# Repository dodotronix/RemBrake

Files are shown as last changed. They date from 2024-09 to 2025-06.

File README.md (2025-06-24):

# RemBrake - remote brake system for handbikes 

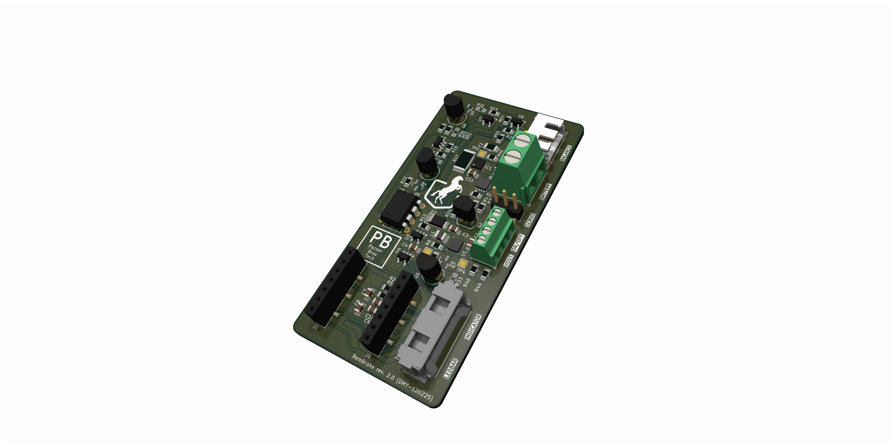
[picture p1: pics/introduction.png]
PCB picture


## Introduction
- TODO explain what the RemBrake, why we decided to create this project

### Assembling RemBrake
- TODO explain how to use the kicad data
- TODO how to solder the modules on the RemBrake PCB
- TODO how to connect the wires

### Prepare the module 
1) load the circuitpython to the QT Py RP2040
2) press and hold BOOT button and then press RST button
3) you should see now RPI partition mounted to your PC 
4) download CircuitPython bootloader (.uf2 file) from [circuitpython.org](https://circuitpython.org/board/adafruit_qtpy_rp2040/) 
5) drag and drop the file onto the partition
6) it takes few moments and you should see your partition name turn to CIRCUITPYTHON

### Upload RemBrake files + necessary modules
1) go to the folder fw folder
2) run $ make prepare
3) move the folder target to your CIRCPITPYTHON partition

## Features
- TODO how the PCB behaves (charging, running, error)
- TODO what the different colors mean

## Possible further development
- Bidirectional remote contoller that the assistant can see the battery status
- Accelerometer feedback, to adjust braking power according to the situation
- Using hydraulic piston actuator to move with the brake directly, which could shrink significantly the size of the package
- designing custom usb-c charger to avoid the hustle with unprecise power management of the chinese module

## Development
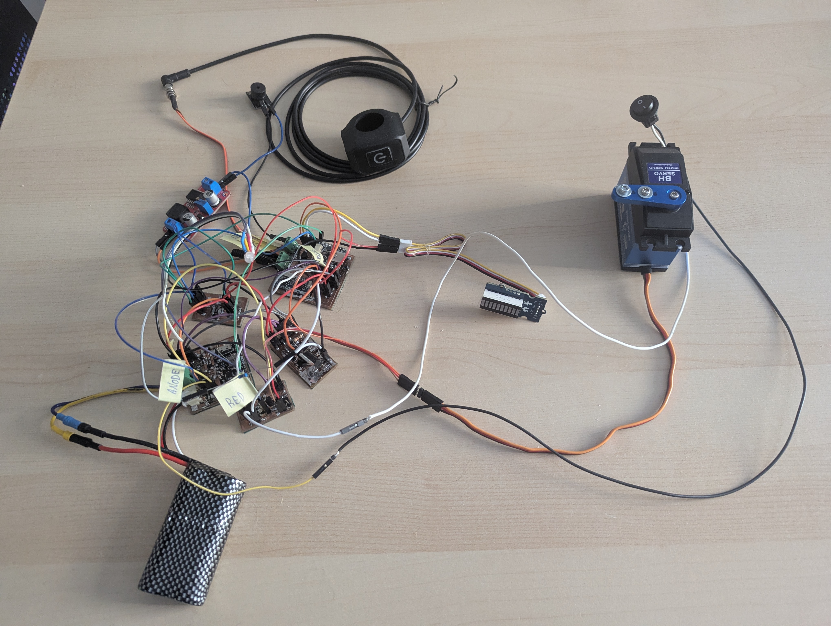
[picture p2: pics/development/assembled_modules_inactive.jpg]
PCB inactive breakout modules

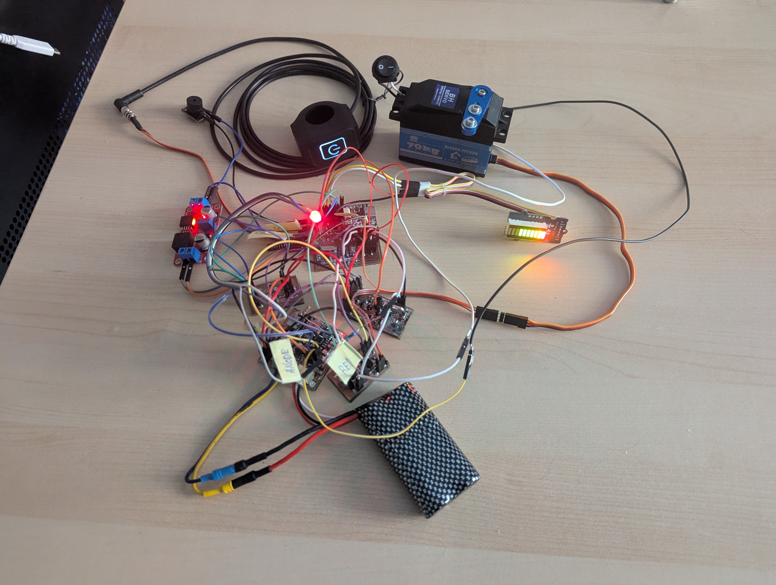
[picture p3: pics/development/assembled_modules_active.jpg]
PCB active breakout modules


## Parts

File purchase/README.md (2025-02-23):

# Shopping List 

The RemBrake requires a few types of electronic components. These can be
purchased on [farnell.com](farnell.com). A pre-prepared list is already available in the user
space—just click on "Purchase." We designed this board using only components
available there. While we cannot guarantee their availability in the future, as
of 2025, they are all in stock.

We decided to use Farnell due to delivery issues with Mouser. The remaining
components are mainly available on AliExpress. The shopping list is below.

| Product | Description | ID | Place to buy | ~price |
|:----:|:----:|:----:|:----:|:----:|
| MCU module | PyQt RP2040 circuitpython supported platform | ADA048 | [link](https://rpishop.cz/adafruit/4248-adafruit-qt-py-rp2040.html) | 349 CZK | 
| USB-C battery charger | Type-C USB 2S BMS 15W 8.4V 1.5A Lithium Battery Charging Boost Module| 2S 8.4V Balanced | [link](https://www.aliexpress.com/item/1005004682732678.html?spm=a2g0o.detail.similar_items.1.16cc8NKk8NKkxb&utparam-url=scene%3Aimage_search%7Cquery_from%3Adetail_bigimg&algo_pvid=c14208da-fe99-42b6-8ce6-5573abc3a80f&algo_exp_id=c14208da-fe99-42b6-8ce6-5573abc3a80f&pdp_ext_f=%7B%22order%22%3A%22200%22%7D&pdp_npi=4%40dis%21CZK%2115.17%2115.17%21%21%210.62%210.62%21%40210390c917403219859821546e6282%2112000030086170587%21sea%21CZ%212328287499%21X) | 15.17 CZK |
| RF transmitter | 1 Channel Wireless RF Remote Control with EV1527 Code, 433 MHz | 1 | [link](https://www.aliexpress.com/item/1005004808801287.html?spm=a2g0o.order_detail.order_detail_item.3.8201f19ccRamzA) | 66.78 CZK |
| RF receiver | 433mhz RF Receiver Learning Code Decoder Module 433 mhz Wireless | 1M | [link](https://www.aliexpress.com/item/1005005452556397.html?spm=a2g0o.order_detail.order_detail_item.3.1109f19cpt4WAQ) | 76.32 CZK | 
| DC/DC Boost module | 5A DC-DC Step Up Power Module Boost Volt Converter 3.3V-35V To 5V 6V 9V 12V 24V | XL6019 | [link](https://www.aliexpress.com/item/4000003691452.html?spm=a2g0o.order_list.order_list_main.80.49721802dWw1Nm) | 24.38 CZK|
| Li-on 2S Battery | | | [link]() | |
| Servo | Digital maxi BH Servo 565-HV320 200g/0,16s/72kg BH Servo | 565-HV320 | [link](https://www.bighobby.cz/digitalni-maxi-bh-servo-565-hv320-200g-0-16s-72kg-bh-servo/) | 1 390 CZK |
| USB-C connector | | | [link]() | | 
| Handlebars button | Light / audio system switch for motorbikes | 15-kf-sw07m | [link](https://www.truckmall.cz/spinac-svetel-predatoru-zvukovych-systemu-na-motocykl-p349914/) | 194 CZK |
| Handlebars button cable | CAZN M5 Connector 4 PIN Straight Angle | NO.050001 | [link](https://www.aliexpress.com/item/1005006236934068.html?spm=a2g0o.order_detail.order_detail_item.3.314ef19c8xBOQw) | 88.02 CZK |
| Handlebars button connector | CAZN M5 flange socket 4 PIN pin plug male | NO.050015 | [link](https://www.aliexpress.com/item/1005006236540760.html?spm=a2g0o.order_detail.order_detail_item.11.314ef19c8xBOQw) | 62.83 CZK | 

remaining components have to be bought on TME.eu

| Product | TME ID | ~price/unit | quantity |
|:----:|:----:|:----:|:----:|
| Balance connector (PCB) | [S3B-XH-SM4-TB](https://www.tme.eu/cz/en/details/s3b-xh-sm4-tb/raster-signal-connectors-2-50mm/jst/) | 6.923 CZK| 1 |
| Balance connector (cable) | [XHP-3](https://www.tme.eu/cz/en/details/xhp-3/raster-signal-connectors-2-50mm/jst/) | 2.0645 CZK| 1 |
| RGB LED 4.8mm | [OSTAPA56A2A](https://www.tme.eu/cz/en/details/ostapa56a2a/tht-leds-round/optosupply/) | 22.294 CZK| 1 |
| PCB terminal block (2 pins) 5mm pitch | [DG128-5.0-02P14](https://www.tme.eu/cz/en/details/dg128-5.0-02p14/pcb-terminal-blocks/degson-electronics/dg128-5-0-02p-14/) | 6.496 CZK| 1 |
| PCB terminal block (4 pins) 2.54mm pitch| [1725672](https://www.tme.eu/cz/en/details/mpt0.5_4-2.54/pcb-terminal-blocks/phoenix-contact/1725672/) | 47.35 CZK| 1 |
| Connector pin strip - socket | [BLLP5SMD20Z](https://www.tme.eu/cz/en/details/bllp5smd20z/pin-headers/fischer-elektronik/10027098/) | 50.17 CZK| 1 |

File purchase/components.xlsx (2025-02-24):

Part Number | Quantity | Line Note
1634656 | 5 | Main switch (waterproof) | R13-112F8-02-BB-2A
3932127 | 5 | Charging indicator | 104020006
1830935 | 5 | 3v3 LDO | XC6220B331MR-G
3007429 | 5 | 5V DC/DC converter | TPS62140RGTR
3404609 | 5 | Ideal Diode | MAX40200AUK+T
4027957 | 5 | BMS chip | LTC2943IDD#TRPBF
3589297 | 5 | Voltage detector | APX803L-40W5-7
3121177 | 5 | 555 casovac THT | LM555CN/NOPB
1022399 | 5 | Buzzer 12V | ABI-010-RC
2533224 | 5 | Schottky diode SOD 123 | MBR0520
3564732 | 10 | Current fuses | MP005472
2914017 | 5 | DPS socket, CLIK-Mate 3 pin | 502494-0370
1617068 | 5 | DPS socket, CLIK-Mate 4 pin | 502494-0470
3221826 | 5 | DPS socket, CLIK-Mate 8 pin | 502494-0870
2913997 | 5 | DPS connector, CLIK-Mate 3 pin | 502439-0300
1617057 | 5 | DPS connector, CLIK-Mate 4 pin | 502439-0400
3864009 | 5 | DPS connector, CLIK-Mate 8 pin | 502439-0800
2313700 | 100 | Contacts CLIK-Mate | 502438-0000
2530074 | 5 | 2.2uH inductor for DC/DC converter | DFE252012P-2R2M=P2
4553395 | 5 | Transistor SMD BC847 | BC847C
3772839 | 5 | P-Channel MOSFET | SIS415DNT-T1-GE3
2309112 | 40 | Resistor 0R 805 | MC0805S8F0000T5E
3951690 | 10 | Current sense resistor 0.01 2512 1% | PE2512FKE070R01L
3495998 | 10 | Resistor 200 805 5% | RC0805FR-07200RL
9237666 | 10 | Resistor 2k7 805 1% | RC0805FR-072K7L
3496134 | 10 | Resistor 5k1 805 5% | RC0805JR-075K1L
4139748 | 40 | Resistor 10k 805 | CRCW080510K0FKEC
4013422 | 10 | Resistor 100k 805 5% | RC0805JR-10100KL
3952338 | 10 | Resistor 590k 805 1% | RC0805FR-07590KL
3019860 | 10 | Capacitor 680pF 10% 805 | CC0805KRX7R9BB681
4539029 | 10 | Capacitor 0.1uF 10% 805 | CL21B104KBCNNND
3785973 | 10 | Capacitor 220nF 10% 805 | GRM21AR72A224KAC5K
3013481 | 10 | Capacitor 1uF 10% 805 | CL21B105KAFNNNE
4327048 | 10 | Capacitor 10 uF 10% 805 | GRM21BC80J106KE19L
4361089 | 10 | Capacitor 22uF 10 % 805 | GRM21BC80J226ME51L
3013465 | 10 | Capacitor 47uF 10% 805 | CL21A476MQCLRNC

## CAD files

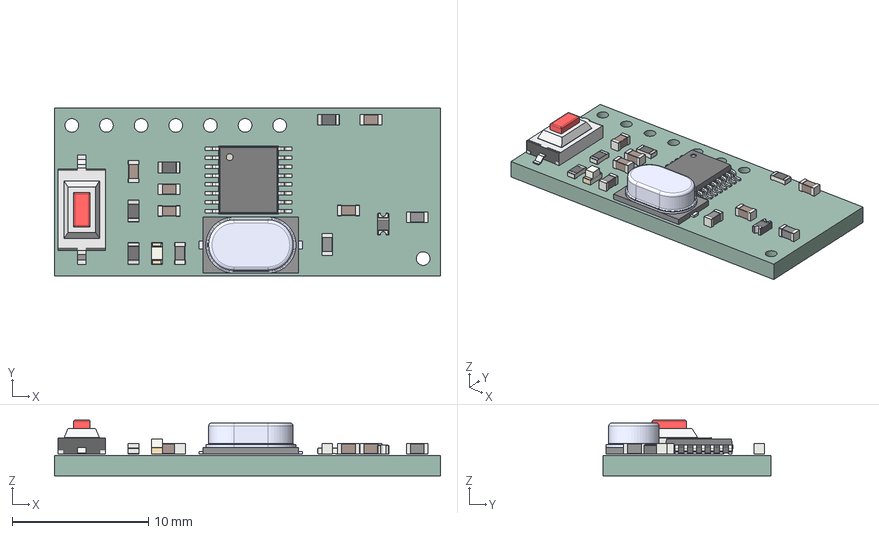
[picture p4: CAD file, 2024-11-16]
design/RFController.step
28.3 x 12.3 x 4.09 mm
C_0603_1608Metric x 5
R_0603_1608Metric x 4
L_0603_1608Metric x 3
TSSOP-16_4.4x5mm_P0.65mm
LED_0603_1608Metric
SW_SPST_CK_RS282G05A3
ECS-160-20-3X-TR
D_0603_1608Metric
RFController_PCB

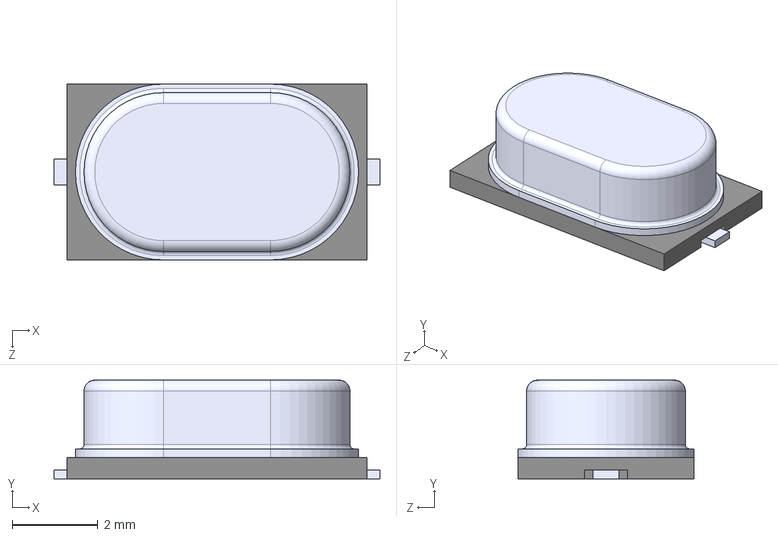
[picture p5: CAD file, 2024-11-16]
design/ECS-160-20-3X-TR.step
7.60 x 2.30 x 4.10 mm

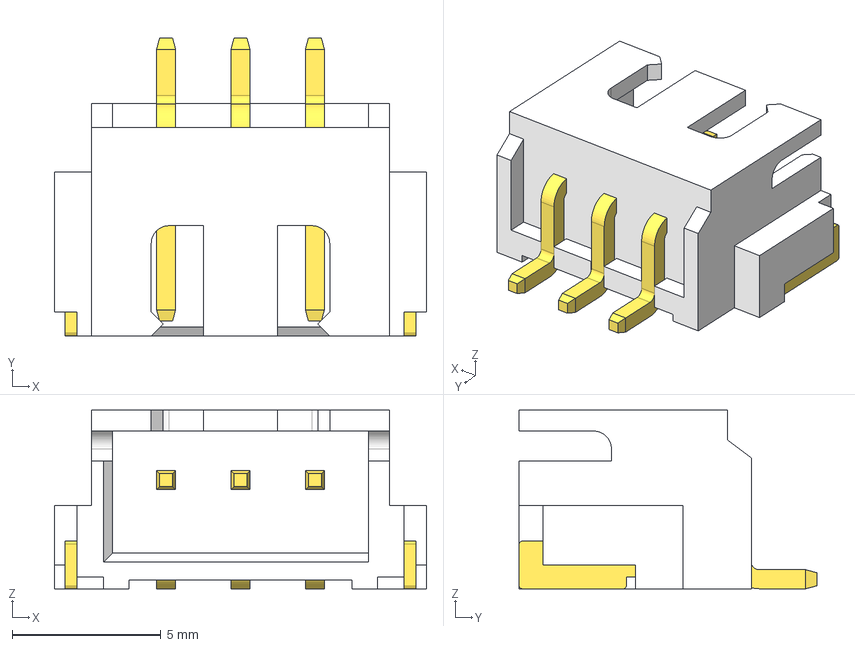
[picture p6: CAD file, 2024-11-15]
design/S3B-XH-SM4-TB.step
12.5 x 10.0 x 6.00 mm

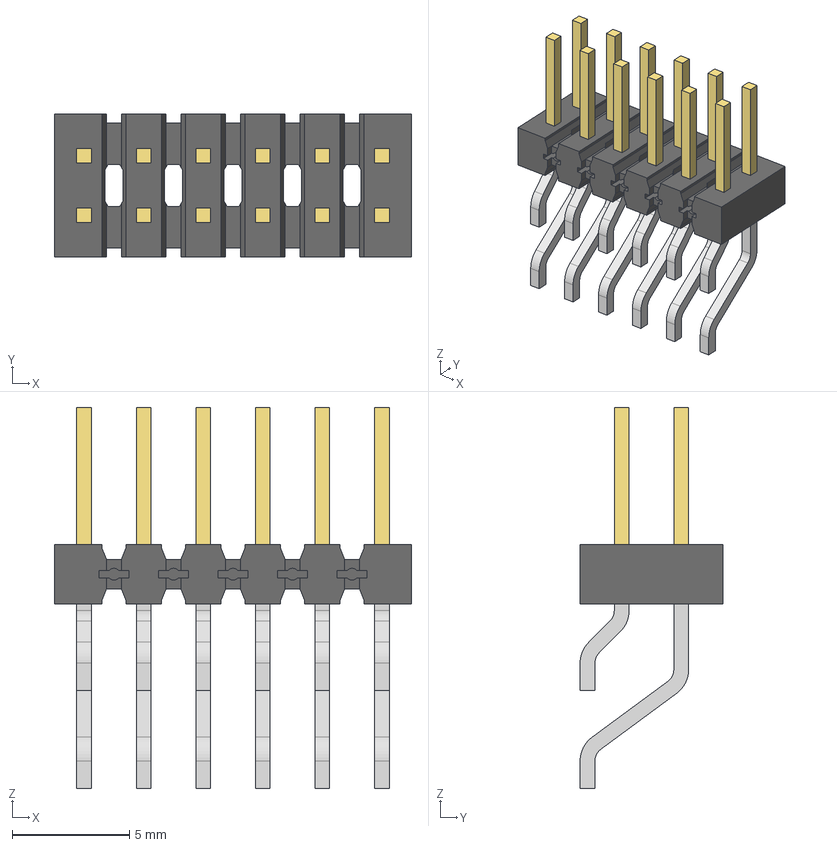
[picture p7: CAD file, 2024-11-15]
design/TSM-106-01-L-DH-TR.stp
15.2 x 6.10 x 16.3 mm
TSM-106-01-DH_body
T-1S6-09-L(-01-6-DH)
T-1S6-09-L(-01-6-DH)2

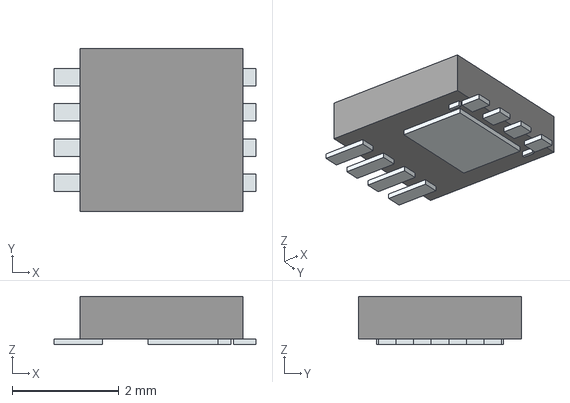
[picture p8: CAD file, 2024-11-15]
design/SIS415DNT-T1-GE3.stp
3.78 x 3.05 x 0.9 mm
Pins

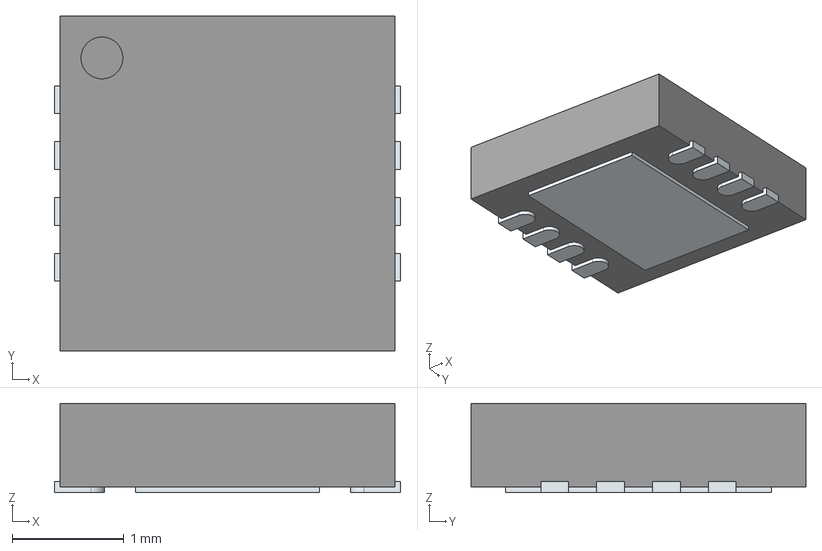
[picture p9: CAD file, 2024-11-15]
design/LTC2943IDD#TRPBF.stp
3.10 x 3.00 x 0.8 mm
ThermalPin
PinsArrayLR

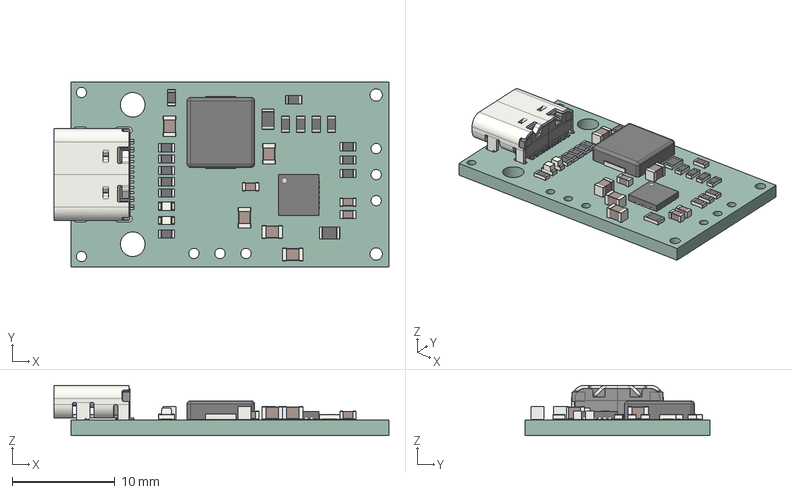
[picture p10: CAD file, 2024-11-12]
design/USBcharger.step
32.7 x 18.0 x 4.91 mm
R_0603_1608Metric x 15
C_0603_1608Metric x 3
C_0805_2012Metric x 5
R_0805_2012Metric x 2
L_APV_APH0620
LED_0603_1608Metric x 2
QFN-24-1EP_4x4mm_P0.5mm_EP2.6x2.6mm
USB_C_Receptacle_GCT_USB4105-xx-A_16P_TopMnt_Horizontal
USBcharger_PCB

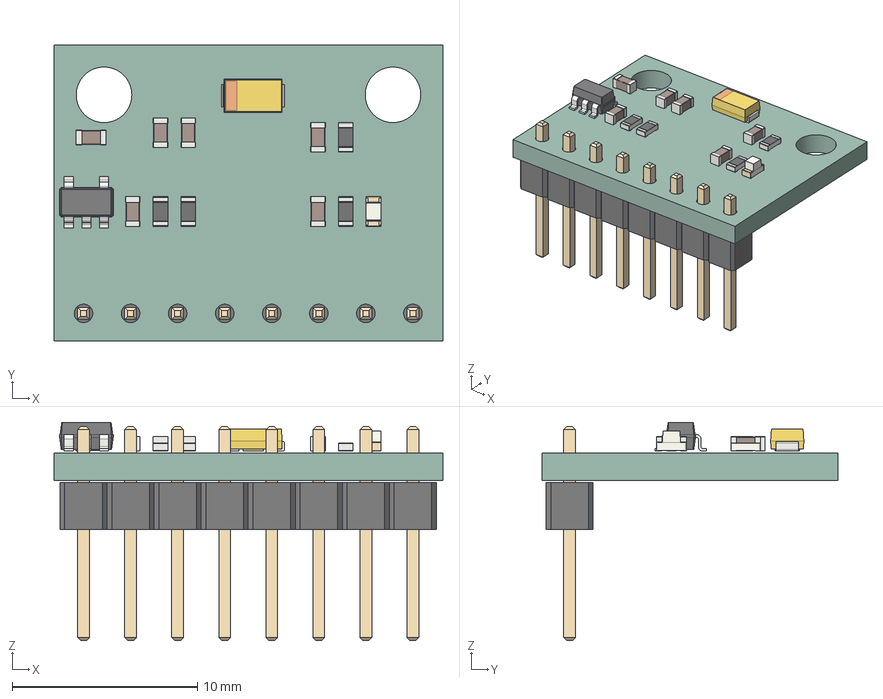
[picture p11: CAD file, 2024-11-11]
design/AccelSensor.step
21.0 x 16.0 x 11.8 mm
R_0603_1608Metric x 4
C_0603_1608Metric x 6
SOT-23-5
CP_EIA-3216-10_Kemet-I
LED_0603_1608Metric
PinHeader_1x08_P2.54mm_Vertical
AccelSensor_PCB

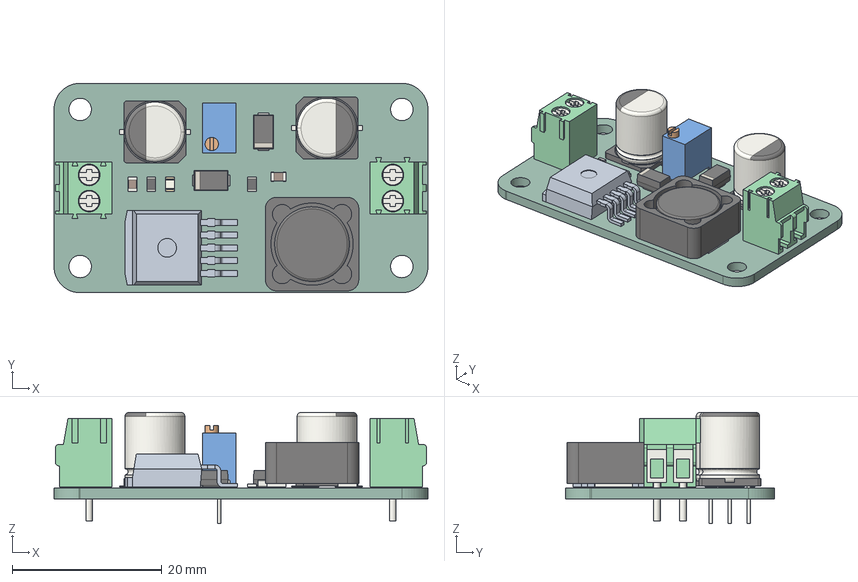
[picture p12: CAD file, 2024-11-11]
design/BoostConverter.step
50.0 x 28.0 x 14.9 mm
TerminalBlock_Phoenix_PT-1,5-2-3.5-H_1x02_P3.50mm_Horizontal x 2
C_0805_2012Metric x 2
CP_Elec_8x10 x 2
D_SMA x 2
BoostConverter 1.5.1
LED_0805_2012Metric
L_Bourns_SRR1260
Potentiometer_Bourns_3266Y_Vertical
R_0805_2012Metric x 2
BoostConverter_PCB

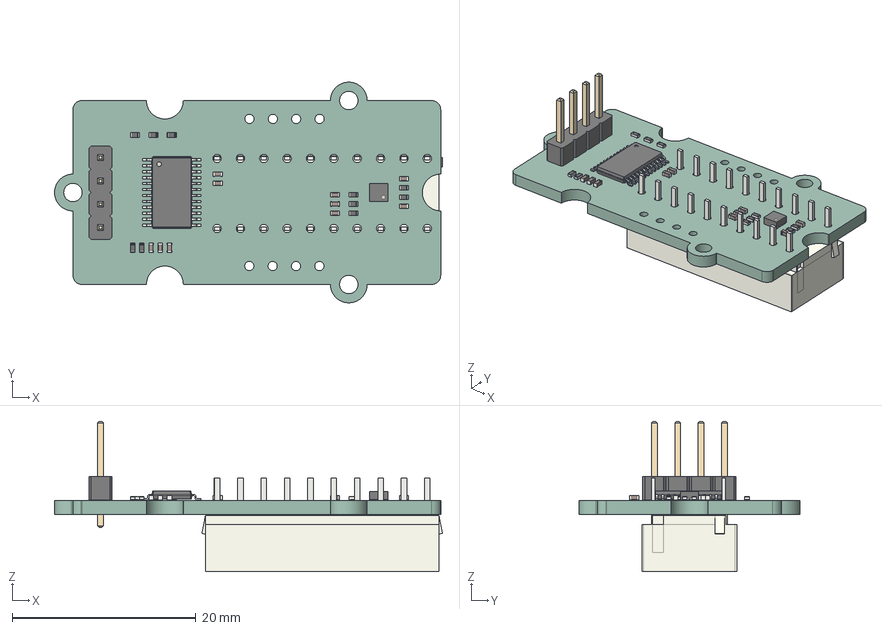
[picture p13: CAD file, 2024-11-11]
design/LEDbar.step
42.2 x 24.0 x 16.3 mm
C_0402_1005Metric x 10
TSSOP-24_4.4x7.8mm_P0.65mm
DFN-8-1EP_2x2mm_P0.5mm_EP1.05x1.75mm
R_0402_1005Metric x 10
PinHeader_1x04_P2.54mm_Vertical
HLCP-J100
LEDbar_PCB

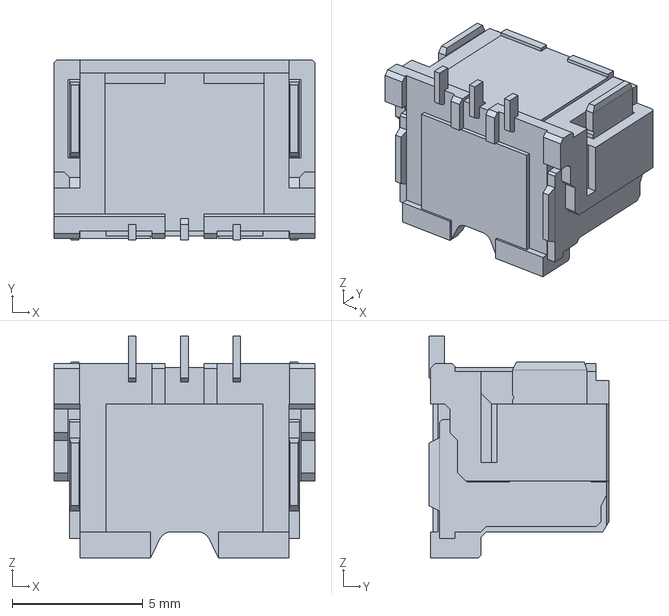
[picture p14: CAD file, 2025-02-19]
design/5024940370.stp
10.0 x 6.90 x 8.50 mm

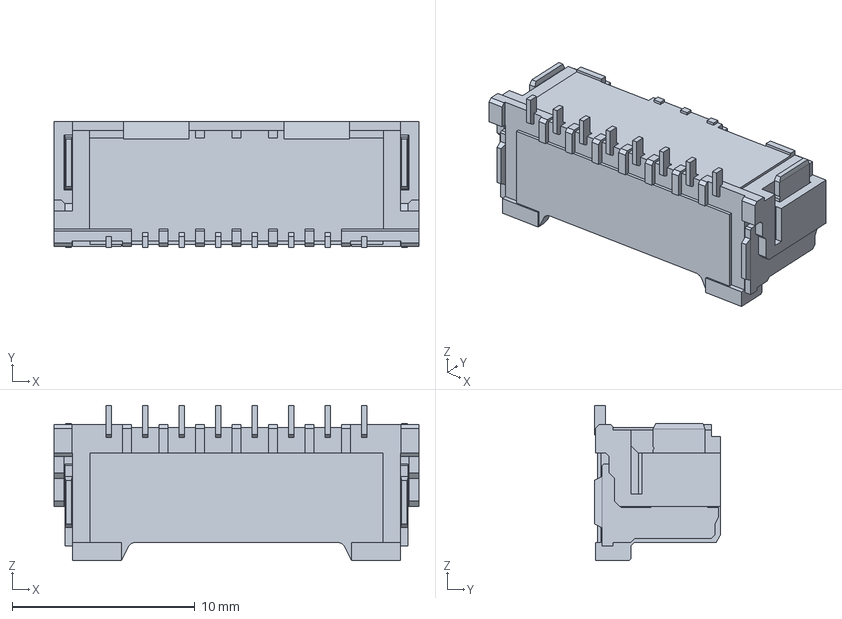
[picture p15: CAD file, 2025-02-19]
design/5024940870.stp
20.0 x 6.90 x 8.50 mm

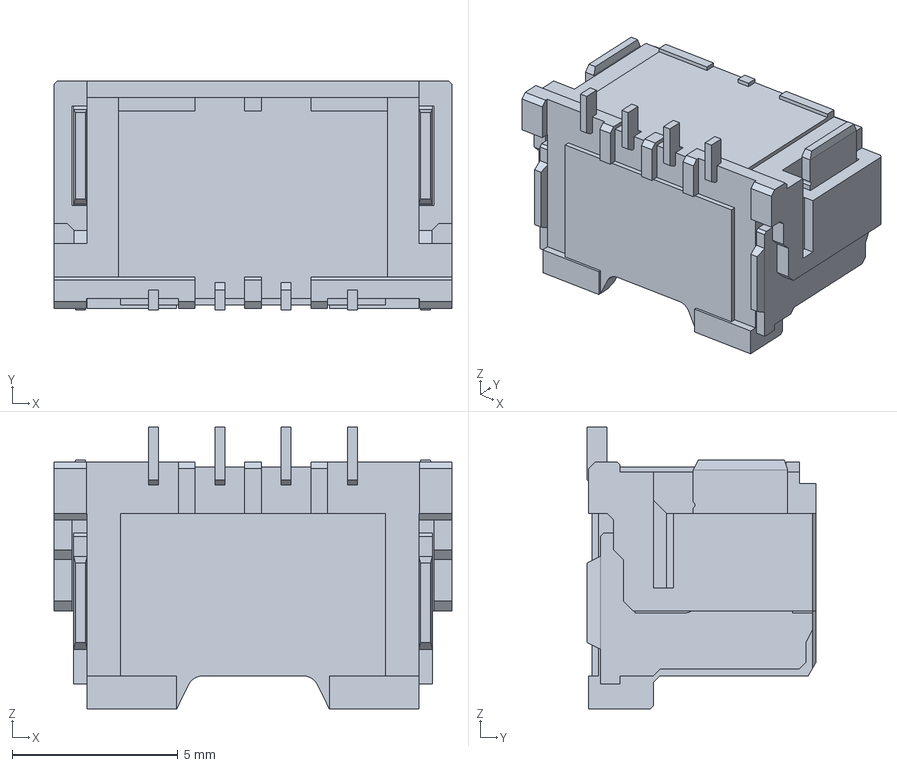
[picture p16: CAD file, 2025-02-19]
design/5024940470.stp
12.0 x 6.90 x 8.50 mm

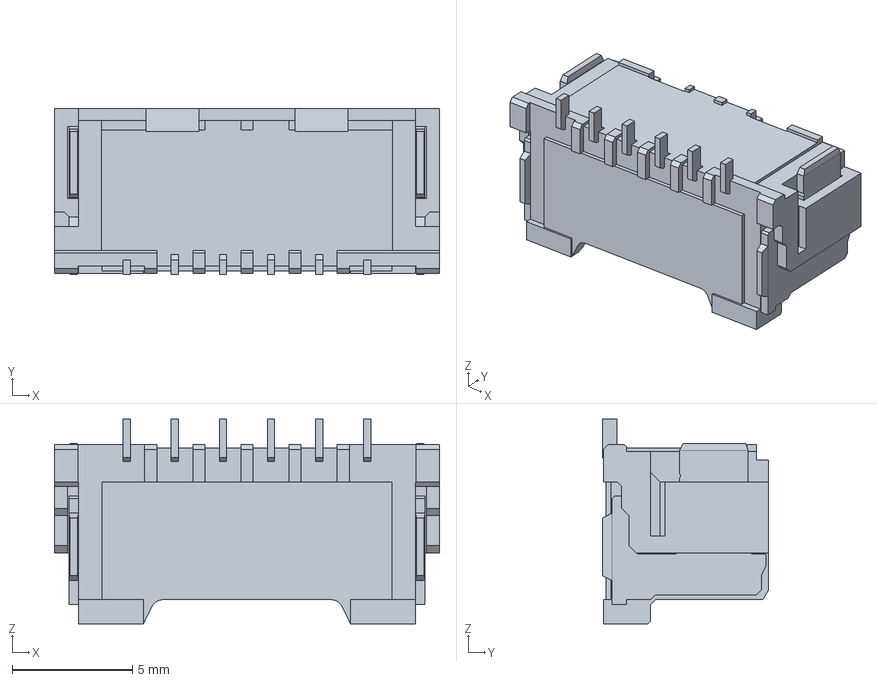
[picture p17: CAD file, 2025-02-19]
design/5024940670.stp
16.0 x 6.90 x 8.50 mm

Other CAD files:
design/TPS62140ARGTR.stp
design/m5_3contacts_out_thread.stp
design/m5_3contacts_in_thread.stp

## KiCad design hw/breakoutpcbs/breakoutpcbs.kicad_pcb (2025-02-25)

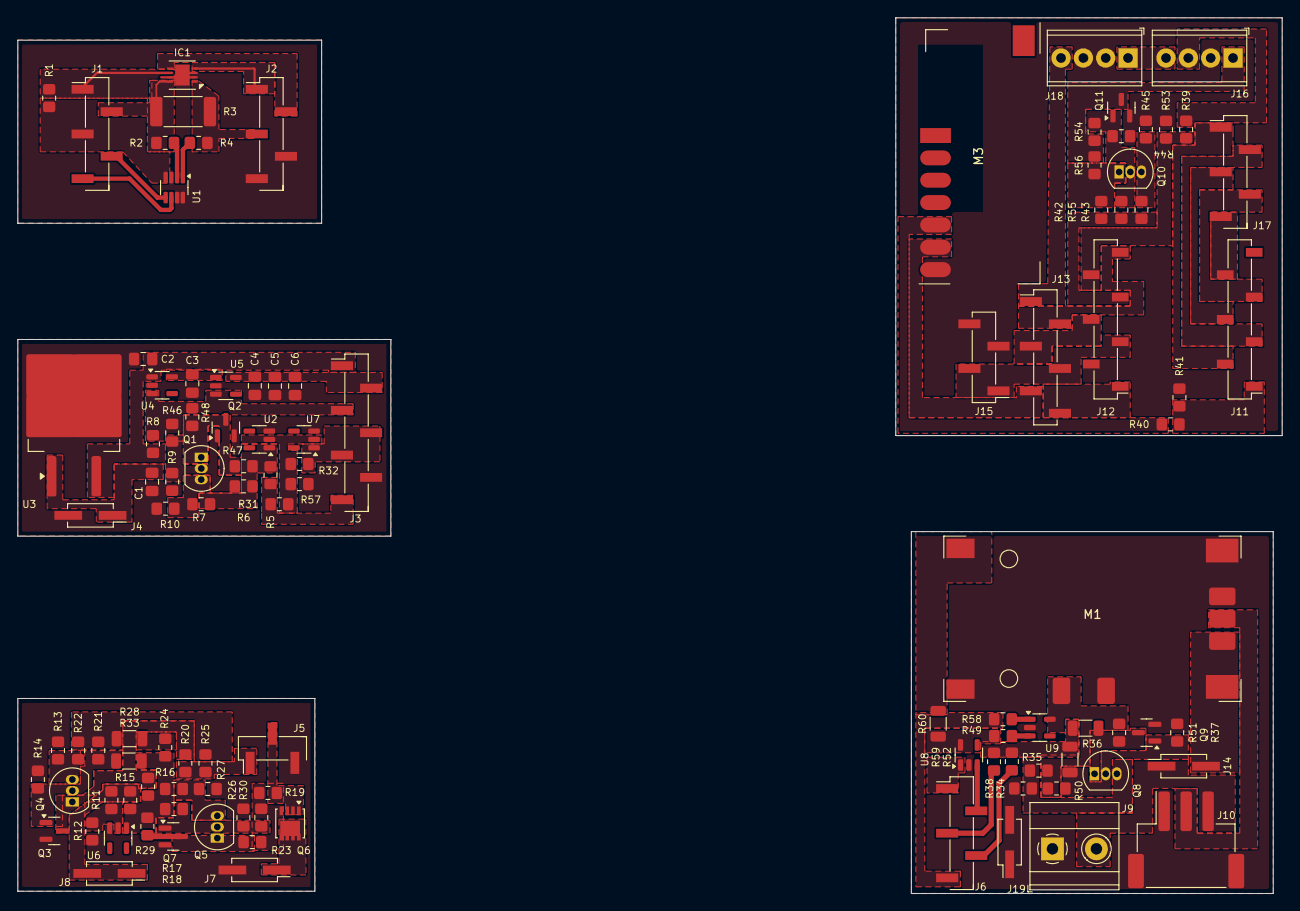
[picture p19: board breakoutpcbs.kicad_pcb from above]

Board: 2 copper layers, 143.8 x 99.6 mm, 108 parts (0 on the bottom side), 80 nets.

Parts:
C1, C2: 0.1uF; C_0805_2012Metric_Pad1.18x1.45mm_HandSolder
C3: 10uF; C_0805_2012Metric_Pad1.18x1.45mm_HandSolder
C4, C5, C6: 22uF; C_0805_2012Metric_Pad1.18x1.45mm_HandSolder
IC1: LTC2943IDD#TRPBF; DFN-8-1EP_3x3mm_P0.5mm_EP1.66x2.38mm
J1, J2, J6, J17: Conn_01x05; PinHeader_1x05_P2.54mm_Vertical_SMD_Pin1Left
J3: Conn_01x07; PinHeader_1x07_P2.54mm_Vertical_SMD_Pin1Left
J4, J7, J8, J14, J19: Conn_01x02; PinHeader_2x01_P2.54mm_Vertical_SMD
J5: Conn_01x03; PinHeader_1x03_P2.54mm_Vertical_SMD_Pin1Left
J9: Screw_Terminal_01x02; TerminalBlock_Phoenix_MKDS-1,5-2_1x02_P5.00mm_Horizontal
J10: Conn_01x03_MountingPin; JST_XH_S3B-XH-SM4-TB_1x03-1MP_P2.50mm_Horizontal
J11, J12: Conn_01x07; PinSocket_1x07_P2.54mm_Vertical_SMD_Pin1Left
J13: Conn_01x06; PinHeader_1x06_P2.54mm_Vertical_SMD_Pin1Left
J15: Conn_01x04; PinHeader_1x04_P2.54mm_Vertical_SMD_Pin1Left
J16, J18: Screw_Terminal_01x04; TerminalBlock_Phoenix_MPT-0,5-4-2.54_1x04_P2.54mm_Horizontal
M1: USBC_charger
M3: RF_controller
Q1, Q4, Q5, Q8, Q10: BC337; TO-92_Inline
Q2, Q3, Q7, Q9, Q11: BC847; SOT-23
Q6: SiS415DNT; Vishay_PowerPAK_1212-8_Single
R1, R5, R8, R15, R19, R23, R30, R32, R49, R52, R57: 10k; R_0805_2012Metric_Pad1.20x1.40mm_HandSolder
R2, R4: 10; R_0805_2012Metric_Pad1.20x1.40mm_HandSolder
R3: 001R; R_2512_6332Metric_Pad1.40x3.35mm_HandSolder
R6, R7, R10, R13, R16, R20, R24, R25, R27, R31, R38, R45, R46, R47, R48, R54, R56: 0R; R_0805_2012Metric_Pad1.20x1.40mm_HandSolder
R9, R14, R17, R18, R21, R22, R26, R29, R34, R35, R37, R42, R43, R44, R51, R55: 4k2; R_0805_2012Metric_Pad1.20x1.40mm_HandSolder
R11: 91k; R_0805_2012Metric_Pad1.20x1.40mm_HandSolder
R12: 67k; R_0805_2012Metric_Pad1.20x1.40mm_HandSolder
R28, R33, R36, R50, R60: 0R; R_1206_3216Metric
R39: 12k; R_0805_2012Metric_Pad1.20x1.40mm_HandSolder
R40: 2k7; R_0805_2012Metric_Pad1.20x1.40mm_HandSolder
R41, R53: 4k7; R_0805_2012Metric_Pad1.20x1.40mm_HandSolder
R58, R59: 200R; R_0805_2012Metric_Pad1.20x1.40mm_HandSolder
U1: INA219BxDCN; SOT-23-8
U2, U6, U7: BD48ExxG; SOT-23-5
U3: L7805; TO-263-2
U4: XC6220B331MR; SOT-23-5
U5, U8, U9: MAX40200AUK; SOT-23-5

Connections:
+3V3: J1.3, R1.1, U1.4 (VS)
+3V3_1: C4.1, C5.1, C6.1, J3.2, U5.5 (OUT)
+3V3_2: J6.4, R52.1
+3V3_3: J12.3, J13.4, J15.1, J15.2
+5V: C2.1, J3.1, R8.2, U3.3 (OUT), U4.1 (VIN)
+5V_1: J13.5, M3.6 (V+)
+7.5V: J7.1, Q6.5 (D)
+7V5_1: J13.1, J18.4
/battery_charger/CHARGED (GREEN): J6.5, R58.1
/battery_charger/CHARGING (BLUE): J6.3, R59.2
/battery_charger/EN2: J6.2, U8.3 (EN)
/battery_charger/VBUS1: J6.1, U8.1 (VDD)
/break_control/BALARM1: J11.2, J17.1
/break_control/BUTTON: J16.3, R39.1
/break_control/BUZZ: J12.5, R42.1, R43.1, R55.2
/break_control/BUZZER: J16.1, Q11.3 (C), R54.2, R56.2
/break_control/CHARGING1: J12.4, J13.3
/break_control/DCKI: J11.4, J17.3
/break_control/DI: J11.3, J17.2
/break_control/RF SWITCH: J11.1, R40.1, R41.2
/break_control/SCL: J11.6, J17.5
/break_control/SDA: J11.5, J17.4
/break_control/SERVO: J12.7, J13.2
/break_control/VBUS2: J12.1, J13.6
/break_control/VEXT: J16.4, J18.1
/power_manager_bb/BALARM: IC1.6 (~ALCC), J1.1, R1.2
/power_switch_bbA/EN1: J5.1, R20.1, R25.1
/power_switch_bbA/ONOFF: J8.1, J8.2, R11.2, R15.2
/power_switch_bbA/VBATT: J5.2, Q6.1 (S), Q6.2 (S), Q6.3 (S), R19.1
/power_switch_bbB/EN: J3.4, J3.5, R32.1, U7.1 (VOUT)
/power_switch_bbB/ONOFF: C1.1, J4.1, U3.1 (IN)
/power_switch_bbB/RUNNING: J3.3, R8.1, R46.2, R48.2, U4.3 (CE), U5.3 (EN)
/power_switch_bbB/VBUS: J3.7, R5.2, R31.1
GND: IC1.2 (GND_1), IC1.3 (GND_2), IC1.7 (GND_3), IC1.9 (EP), J2.4, J2.5, U1.3 (GND), U1.7 (A0), U1.8 (A1)
GND1: J5.3, J7.2, Q3.2 (E), Q7.2 (E), R12.1, R13.1, R14.1, R26.1, R27.1, U6.3 (GND)
GND2: C1.2, C2.2, C3.2, C4.2, C5.2, C6.2, J3.6, J4.2, Q2.2 (E), R9.1, R10.1, R57.2, U2.3 (GND), U3.2 (GND), U4.2 (GND), U5.2 (GND), U7.3 (GND)
GND3: J9.1, J10.1, J10.MP (MountPin), J19.1, J19.2, M1.2 (GND), M1.5 (BAT-), Q9.2 (E), R37.1, R38.1, U8.2 (GND), U9.2 (GND)
GND4: J12.2, J15.3, J15.4, J16.2, J18.2, J18.3, M3.7 (GND), Q11.2 (E), R41.1, R44.1, R45.1, R53.2
unnamed: IC1.4 (SCL), J2.1
unnamed: IC1.5 (SDA), J2.2
unnamed: IC1.1 (SENSE+), J2.3, R3.2, R4.1
unnamed: IC1.8 (SENSE-), J1.2, R2.1, R3.1
unnamed: J1.4, U1.5 (SCL)
unnamed: J1.5, U1.6 (SDA)
unnamed: J10.2, M1.4 (BM)
unnamed: J9.2, J10.3, J14.1
unnamed: J12.6, R39.2, R53.1
unnamed: J14.2, M1.3 (BAT+)
unnamed: M1.6 (LED), R34.1, R35.1, R51.1, U9.5 (OUT)
unnamed: M1.1 (Vin), R60.1
unnamed: M3.5 (D0), R40.2
unnamed: Q1.2 (B), Q2.1 (B), R6.2, R9.2, R46.1
unnamed: Q1.1 (C), Q2.3 (C), R47.1, R48.1
unnamed: Q1.3 (E), R7.2, R10.2
unnamed: Q3.1 (B), Q4.2 (B), R14.2, R21.2, R33.1
unnamed: Q3.3 (C), Q4.1 (C), R16.1, R20.2
unnamed: Q4.3 (E), R13.2, R22.2
unnamed: Q5.2 (B), Q7.1 (B), R17.2, R26.2, R30.1
unnamed: Q5.1 (C), Q7.3 (C), R23.1, R29.2
unnamed: Q5.3 (E), R18.2, R27.2
unnamed: Q6.4 (G), R19.2, R23.2, R30.2
unnamed: Q8.2 (B), Q9.1 (B), R34.2, R37.2, R50.2
unnamed: Q8.1 (C), Q9.3 (C), R36.2, R51.2
unnamed: Q8.3 (E), R35.2, R38.2
unnamed: Q10.2 (B), Q11.1 (B), R42.2, R44.2, R54.1
unnamed: Q10.1 (C), R55.1, R56.1
unnamed: Q10.3 (E), R43.2, R45.2
unnamed: R21.1, R22.1, R25.2, R28.1
unnamed: R24.1, R28.2
unnamed: R36.1, R50.1, R52.2, R59.1
unnamed: R4.2, U1.1 (IN+)
unnamed: R2.2, U1.2 (IN-)
unnamed: R31.2, R32.2, R57.1, U2.2 (VDD), U7.2 (VDD)
unnamed: R5.1, R6.1, R7.1, R47.2, U2.1 (VOUT)
unnamed: C3.1, U4.5 (VOUT), U5.1 (VDD)
unnamed: R11.1, R12.2, U6.2 (VDD)
unnamed: R15.1, R16.2, R17.1, R18.1, R24.2, R29.1, R33.2, U6.1 (VOUT)
unnamed: R49.1, R60.2, U8.5 (OUT)
unnamed: R49.2, U9.3 (EN)
unnamed: R58.2, U9.1 (VDD)

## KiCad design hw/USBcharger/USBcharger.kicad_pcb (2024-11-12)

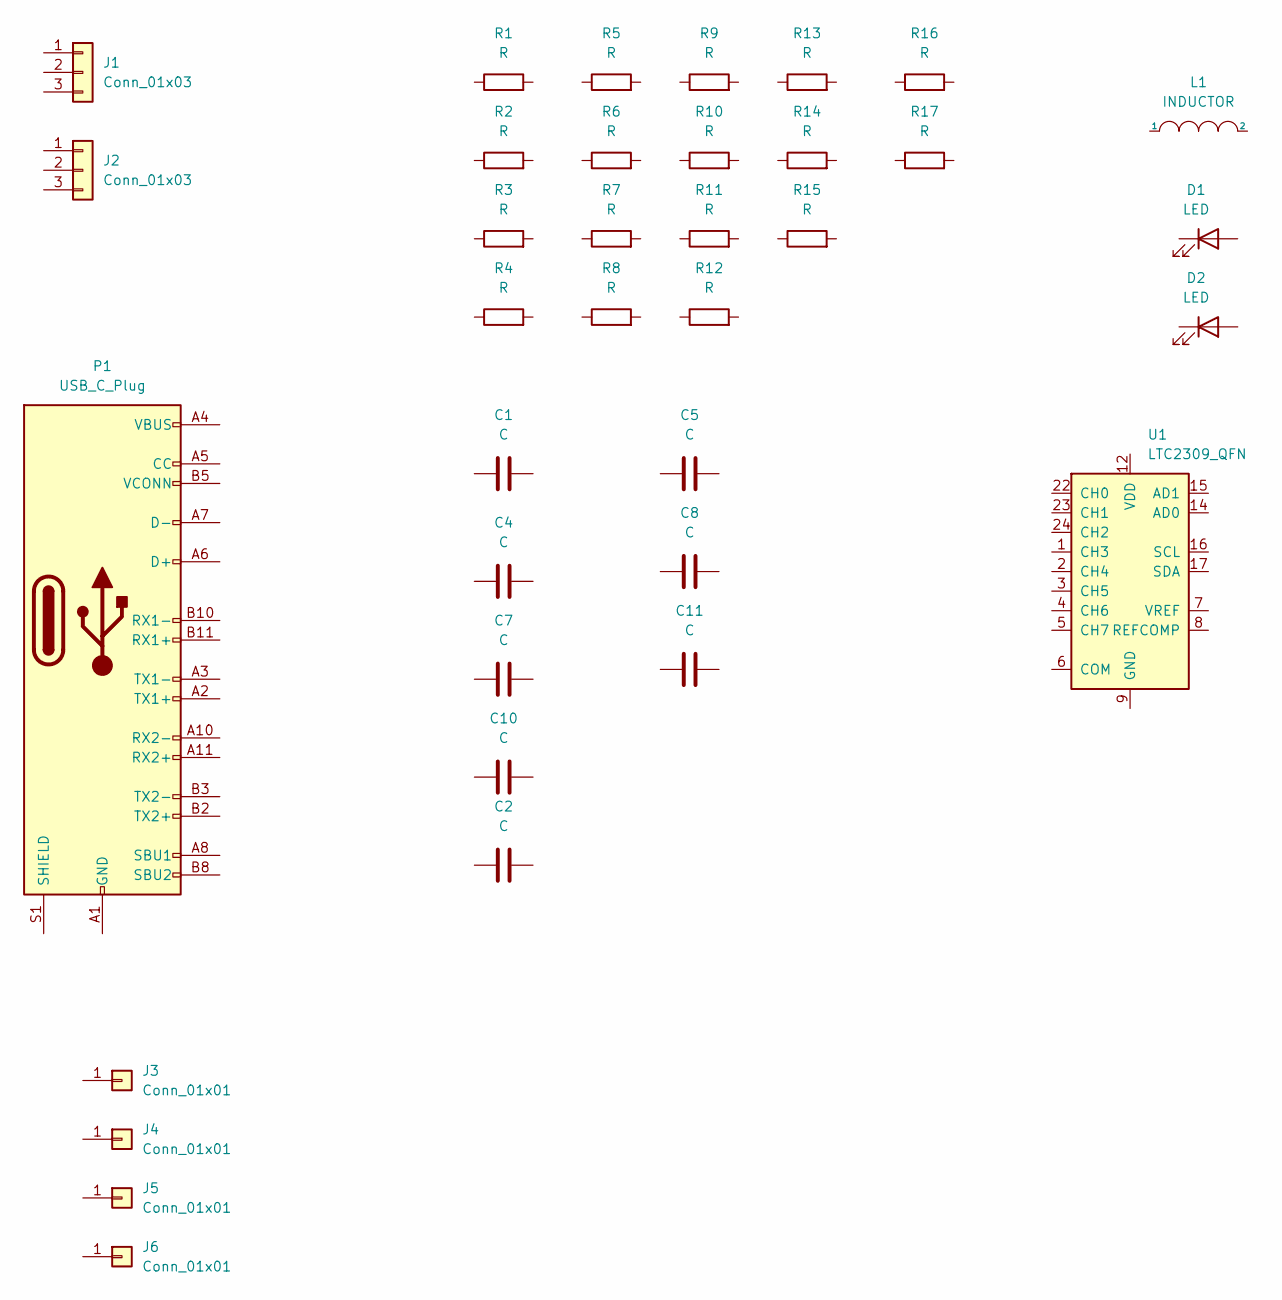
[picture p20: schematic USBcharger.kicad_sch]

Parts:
C1, C2, C4: C; C_0603_1608Metric
C5, C7, C8, C10, C11: C; C_0805_2012Metric
D1, D2: LED; LED_0603_1608Metric
J1, J2: Conn_01x03; PinHeader_1x03_P2.54mm_Vertical
J3, J4: Conn_01x01; TestPoint_THTPad_2.0x2.0mm_Drill1.0mm
J5, J6: Conn_01x01; TestPoint_THTPad_2.5x2.5mm_Drill1.2mm
L1: INDUCTOR; L_APV_APH0620
P1: USB_C_Plug; USB_C_Receptacle_GCT_USB4105-xx-A_16P_TopMnt_Horizontal
R1, R2, R3, R4, R5, R6, R7, R8, R9, R10, R11, R12, R13, R14, R15: R; R_0603_1608Metric
R16, R17: R; R_0805_2012Metric
U1: LTC2309_QFN; QFN-24-1EP_4x4mm_P0.5mm_EP2.6x2.6mm

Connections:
unnamed: P1.A1 (GND), P1.A12 (GND), P1.B1 (GND), P1.B12 (GND)
unnamed: P1.A4 (VBUS), P1.A9 (VBUS), P1.B4 (VBUS), P1.B9 (VBUS)
unnamed: U1.9 (GND), U1.10 (GND), U1.11 (GND), U1.18 (GND), U1.19 (GND), U1.20 (GND), U1.25 (GND)
unnamed: U1.12 (VDD), U1.13 (VDD), U1.21 (VDD)

Board: 11 copper layers, 36 parts (0 on the bottom side), 4 nets, no tracks yet.

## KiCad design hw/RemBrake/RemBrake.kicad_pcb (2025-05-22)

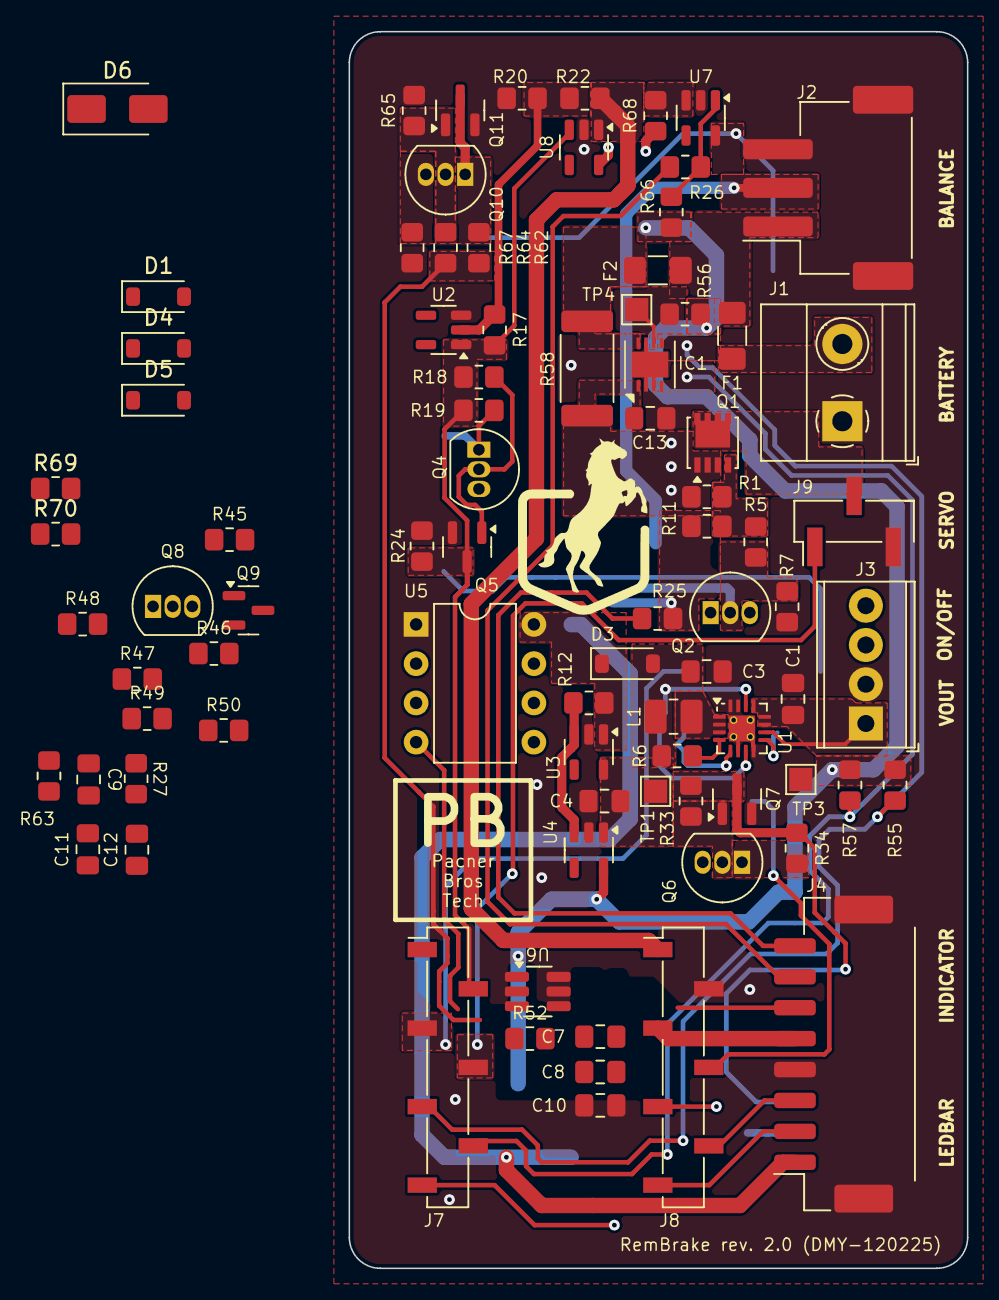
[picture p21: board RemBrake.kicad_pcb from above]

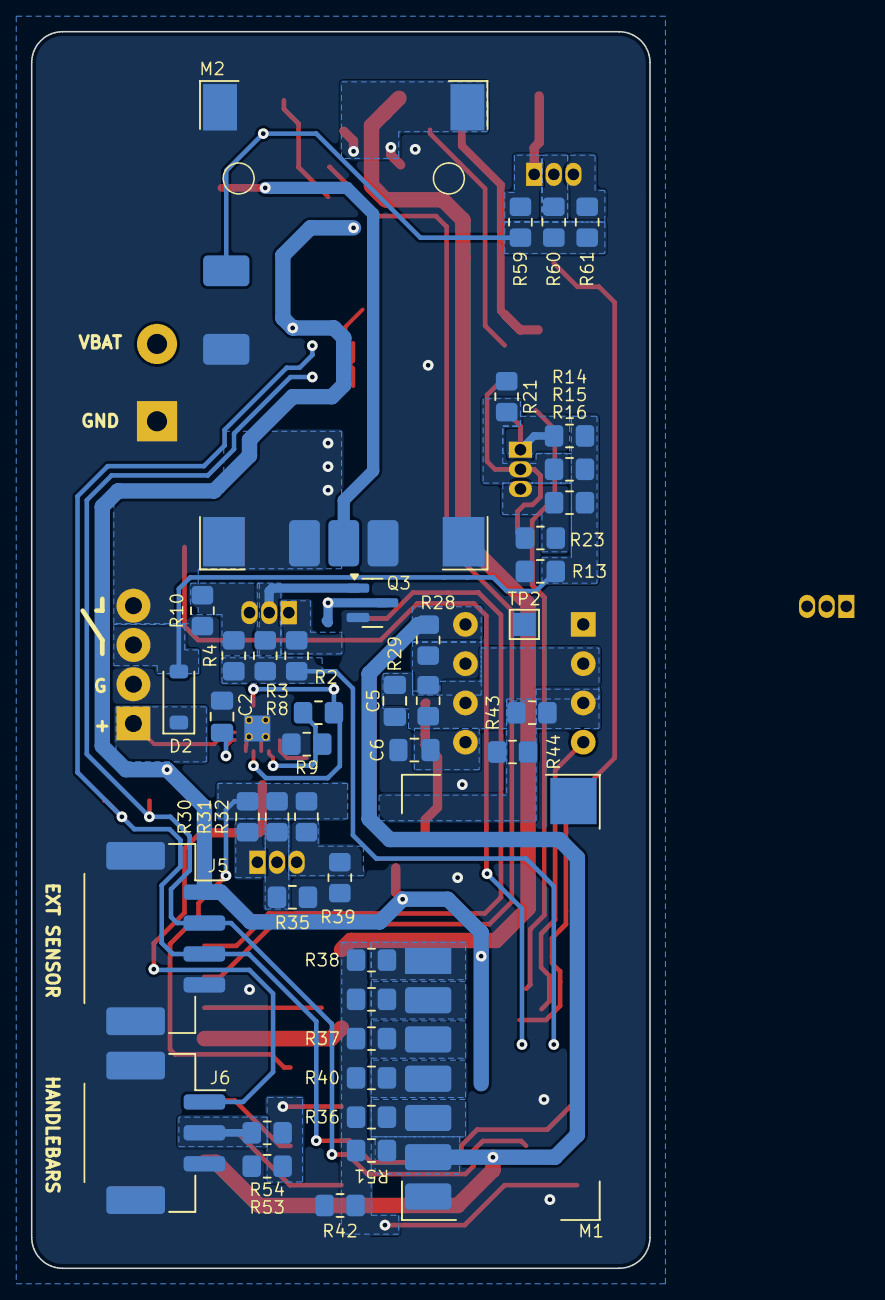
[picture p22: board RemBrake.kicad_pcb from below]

Board: 2 copper layers, 40.0 x 80.0 mm, 127 parts (43 on the bottom side), 71 nets.

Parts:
C1: 10uF; C_0805_2012Metric_Pad1.18x1.45mm_HandSolder
C2, C9: 680pF; C_0805_2012Metric_Pad1.18x1.45mm_HandSolder
C3, C7, C8, C10: 22uF; C_0805_2012Metric_Pad1.18x1.45mm_HandSolder
C4, C5, C6: 0.1uF; C_0805_2012Metric_Pad1.18x1.45mm_HandSolder
C11, C12: 0.33uF; C_0805_2012Metric_Pad1.18x1.45mm_HandSolder
C13: 1uF; C_0805_2012Metric_Pad1.18x1.45mm_HandSolder
D1, D2, D3, D4, D5: MBR0520; D_SOD-123
D6: SS1200; D_SMA
F1, F2: 10A / 24V; Fuse_1206_3216Metric_Pad1.42x1.75mm_HandSolder
IC1: LTC2943IDD#TRPBF; DFN-8-1EP_3x3mm_P0.5mm_EP1.66x2.38mm
J1: Screw_Terminal_01x02; TerminalBlock_Phoenix_MKDS-1,5-2_1x02_P5.00mm_Horizontal
J2: Conn_01x03_MountingPin; JST_XH_S3B-XH-SM4-TB_1x03-1MP_P2.50mm_Horizontal
J3: Screw_Terminal_01x04; TerminalBlock_Phoenix_MPT-0,5-4-2.54_1x04_P2.54mm_Horizontal
J4: Conn_01x08_MountingPin; Molex_CLIK-Mate_502494-0870_1x08-1MP_P2.00mm_Horizontal
J5: Conn_01x04_MountingPin; Molex_CLIK-Mate_502494-0470_1x04-1MP_P2.00mm_Horizontal
J6: Conn_01x03_MountingPin; Molex_CLIK-Mate_502494-0370_1x03-1MP_P2.00mm_Horizontal
J7, J8: Conn_01x07; PinSocket_1x07_P2.54mm_Vertical_SMD_Pin1Left
J9: Conn_01x03; PinHeader_1x03_P2.54mm_Vertical_SMD_Pin1Left
L1: 2.2uH; L_1008_2520Metric_Pad1.43x2.20mm_HandSolder
M1: RF_controller
M2: USBC_charger
Q1: SiS415DNT; Vishay_PowerPAK_1212-8_Single
Q2, Q4, Q6, Q8, Q10: BC337; TO-92_Inline
Q3, Q5, Q7, Q9, Q11: BC847; SOT-23
R1, R5, R11, R12, R17, R24, R29, R42, R44, R54, R55, R56, R57, R63, R66, R68: 10k; R_0805_2012Metric_Pad1.20x1.40mm_HandSolder
R2, R14, R30, R36, R43, R46, R52, R59: 5k1; R_0805_2012Metric_Pad1.20x1.40mm_HandSolder
R3, R4, R15, R16, R21, R31, R32, R35, R37, R38, R40, R41, R47, R48, R60, R61: 5k; R_0805_2012Metric_Pad1.20x1.40mm_HandSolder
R6, R9, R13, R45, R51: 100k; R_0805_2012Metric_Pad1.20x1.40mm_HandSolder
R7, R10, R18, R19, R20, R22, R23, R39, R49, R50, R62, R64, R65, R67, R69, R70: 0R; R_0805_2012Metric_Pad1.20x1.40mm_HandSolder
R8: 536k; R_0805_2012Metric_Pad1.20x1.40mm_HandSolder
R25, R26, R27, R33: 110R; R_0805_2012Metric_Pad1.20x1.40mm_HandSolder
R28, R53: 2k7; R_0805_2012Metric_Pad1.20x1.40mm_HandSolder
R34: 200R; R_0805_2012Metric_Pad1.20x1.40mm_HandSolder
R58: 10mR; R_2512_6332Metric_Pad1.40x3.35mm_HandSolder
TP1, TP2, TP3, TP4: TestPoint_Probe; TestPoint_Pad_1.5x1.5mm
U1: TPS62140; VQFN-16-1EP_3x3mm_P0.5mm_EP1.68x1.68mm_ThermalVias
U2: BD48ExxG; SOT-23-5
U3: XC6220B331MR; SOT-23-5
U4, U7, U8: MAX40200AUK; SOT-23-5
U5: LM555xN; DIP-8_W7.62mm
U6: BD5230G-TR; SOT-23-6_Handsoldering

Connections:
+3V3: C7.1, C8.1, C10.1, J4.5, J5.1, J8.3, R55.1, R56.1, R57.1, R63.1, R66.1, U4.5 (OUT)
+5V: C3.1, D3.2 (A), L1.2, R6.1, R8.1, R12.1, R28.1, R51.1, U1.7 (FSW), U1.14 (VOS), U3.1 (VIN), U5.8 (VCC)
+7.5V: D6.1 (K), J9.2, Q1.5 (D)
/brake_control/BEEP: R51.2, U5.4 (R), U6.1 (VOUT)
/brake_control/BTN: J8.5, R53.2, R54.2
/brake_control/BUZZ: J8.4, R30.2, R31.1, R32.1, R43.2, R44.2
/brake_control/BUZZER: J6.1, Q7.3 (C), R33.1, R34.1
/brake_control/DISPLAY.DCKI: J4.2, J8.7
/brake_control/DISPLAY.DI: J4.3, J8.6
/brake_control/ENABLE: J7.2, Q5.3 (C), R17.1, R18.2, R19.2, R24.2, U2.1 (VOUT), U8.3 (EN)
/brake_control/I2C.SCL: IC1.4 (SCL), J5.2, J7.6, R57.2
/brake_control/I2C.SDA: IC1.5 (SDA), J5.3, J7.5, R55.2
/brake_control/POWER: J7.3, R2.1, R3.1, R4.1, R45.2, R46.1, R47.1, R48.1
/brake_control/READY: J7.1, R52.1
/brake_control/RF SWITCH: J7.7, R36.1, R37.1, R38.1, R40.1, R41.1, R42.2
/brake_control/RUNNIG (RED): R25.1, R69.1, R70.1
/brake_control/SERVO: J7.4, J9.1
/brake_control/STATUS: C9.1, R27.1, R52.2, R62.1, R63.2, R64.1, U6.2 (VDD)
/brake_control/VBUS: D4.2 (A), D5.2 (A), J8.1, R22.1, U8.1 (VDD)
/control_connector/BLUE: J4.6, R27.2
/control_connector/BUTTON: J6.2, R54.1
/control_connector/GREEN: J4.7, R26.2
/control_connector/LED GREEN: R26.1, R66.2, U7.1 (VDD)
/control_connector/RED: J4.8, R25.2
/power_manager/BAT+: F2.1, IC1.8 (SENSE-), R58.1
/power_manager/BM: J2.2, M2.4 (BM)
/power_manager/VBATT: C13.2, IC1.1 (SENSE+), J3.4, M2.3 (BAT+), Q1.1 (S), Q1.2 (S), Q1.3 (S), R1.1, R58.2
/power_switch/BOOST: D1.1 (K), D4.1 (K), J3.1
/power_switch/ON/OFF: D1.2 (A), D2.2 (A), J3.3, R13.2, R14.1, R15.1, R16.1, U1.13 (EN)
GND: C1.2, C2.2, C3.2, C4.2, C5.2, C6.2, C7.2, C8.2, C9.2, C10.2, C11.2, C12.2, C13.1, D6.2 (A), IC1.2 (GND_1), IC1.3 (GND_2), IC1.7 (GND_3), IC1.9 (EP), J1.1, J2.3, J2.MP (MountPin), J3.2, J4.4, J4.MP (MountPin), J5.4, J5.MP (MountPin), J6.3, J6.MP (MountPin), J8.2, J9.3, M1.7 (GND), M2.2 (GND), M2.5 (BAT-), Q3.2 (E), Q5.2 (E), Q7.2 (E), Q9.2 (E), Q11.2 (E), R7.1, R9.2, R10.1, R13.1, R20.2, R21.1, R23.1, R24.1, R35.1, R39.1, R42.1, R44.1, R45.1, R49.1, R50.1, R53.1, R65.1, R67.1, TP2.1, TP3.1, U1.6 (GND), U1.8 (DEF), U1.15 (GND), U1.16 (GND), U1.17 (GND), U2.3 (GND), U3.2 (GND), U4.2 (GND), U5.1 (GND), U6.3 (GND), U7.2 (GND), U8.2 (GND)
unnamed: C1.1, D2.1 (K), U1.10 (VIN), U1.11 (VIN), U1.12 (VIN)
unnamed: IC1.6 (~ALCC), R56.2, TP4.1
unnamed: F1.2, J1.2
unnamed: F1.1, F2.2, J2.1
unnamed: L1.1, U1.1 (SW), U1.2 (SW), U1.3 (SW)
unnamed: M1.5 (D0), R36.2
unnamed: M1.4 (D1), R40.2
unnamed: M1.3 (D2), R37.2
unnamed: M1.2 (D3), R41.2
unnamed: M1.1 (VT), R38.2
unnamed: M2.6 (LED), R59.1, R60.1, R61.1, U7.5 (OUT)
unnamed: M2.1 (Vin), R68.1, U8.5 (OUT)
unnamed: Q1.4 (G), R1.2, R5.2, R11.2
unnamed: Q2.2 (B), Q3.1 (B), R3.2, R5.1, R7.2
unnamed: Q2.1 (C), Q3.3 (C), R2.2, R11.1
unnamed: Q2.3 (E), R4.2, R10.2
unnamed: Q4.2 (B), Q5.1 (B), R15.2, R18.1, R21.2
unnamed: Q4.1 (C), R14.2, R19.1
unnamed: Q4.3 (E), R16.2, R23.2
unnamed: Q6.2 (B), Q7.1 (B), R31.2, R33.2, R35.2
unnamed: Q6.1 (C), R30.1, R34.2
unnamed: Q6.3 (E), R32.2, R39.2
unnamed: Q8.2 (B), Q9.1 (B), R47.2, R49.2, R70.2
unnamed: Q8.1 (C), Q9.3 (C), R46.2, R69.2
unnamed: Q8.3 (E), R48.2, R50.2
unnamed: Q10.2 (B), Q11.1 (B), R60.2, R62.2, R65.2
unnamed: Q10.1 (C), Q11.3 (C), R59.2, R64.2
unnamed: Q10.3 (E), R61.2, R67.2
unnamed: R8.2, R9.1, U1.5 (FB)
unnamed: R6.2, U1.4 (PG)
unnamed: C2.1, U1.9 (SS/TR)
unnamed: R17.2, R20.1, R22.2, U2.2 (VDD)
unnamed: R12.2, U3.3 (CE), U4.3 (EN)
unnamed: C4.1, TP1.1, U3.5 (VOUT), U4.1 (VDD)
unnamed: C6.1, U5.5 (CV)
unnamed: R28.2, R29.1, U5.7 (DIS)
unnamed: R43.1, U5.3 (Q)
unnamed: C5.1, R29.2, U5.2 (TR), U5.6 (THR)
unnamed: C11.1, C12.1, U6.5 (CT)
unnamed: R68.2, U7.3 (EN)
VDD: D3.1 (K), D5.1 (K), J4.1, M1.6 (V+)

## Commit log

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2024-10-26 created kicad project
    [4ch_transmitter.kicad_sch, RemBreak.kicad_pcb, RemBreak.kicad_sch, charging_module.kicad_sch]
2024-10-26 charging module
    [charging_module.kicad_sch]
2024-10-28 deleted redundant sheet
    [4ch_transmitter.kicad_sch]
2024-10-28 first version of the remote break main board
    [RemBreak.kicad_sch]
2024-10-30 schematics supporting different pinout of BJTs and removed accelerometer
    [RemBreak.kicad_sch, power_control.kicad_sch]
2024-11-09 created model of the grove seeed studio led bar
    [LEDbar.kicad_pcb, LEDbar.kicad_sch]
2024-11-09 first version of the led bar finished
    [LEDbar.kicad_pcb, LEDbar.kicad_sch]
2024-11-09 first version of mpu-6050 amazon breakout board replica
    [AccelSensor.kicad_pcb, AccelSensor.kicad_sch]
2024-11-09 usb charger inprogress missing few 3d models
    [USBcharger.kicad_pcb, USBcharger.kicad_sch]
2024-11-09 schematics and cut edges ready
    [BoostConverter.kicad_pcb, BoostConverter.kicad_sch]
2024-11-10 created model of the chinese charger module
    [USBcharger.kicad_pcb, USBcharger.kicad_sch]
2024-11-10 assambled model of the boost dcdc convertor from china
    [BoostConverter.kicad_pcb, BoostConverter.kicad_sch]
2024-11-10 ledbar project - updated settings to generate step file
    [LEDbar.kicad_pcb]
2024-11-10 project settings to generate step file
    [BoostConverter.kicad_pcb]
2024-11-10 updated version of the document
    [AccelSensor.kicad_pcb, AccelSensor.kicad_sch]
2024-11-10 updated version of the project for newer kicad
    [USBcharger.kicad_pcb]
2024-11-11 updated USBcharger module model
    [RemBreak.kicad_pcb, RemBreak.kicad_sch, power_switch.kicad_sch]
2024-11-11 generated step files to add to the 3d mechanical design
    [AccelSensor.step, BoostConverter.step, LEDbar.step, USBcharger.step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]
2024-11-11 temporary schematics sheets
    [control_unit.kicad_sch, power_control.kicad_sch]
2024-11-11 model of the rf control pcb from china
    [RFController.kicad_sch]
2024-11-11 rf control pcb from china
    [RFController.kicad_pcb]
2024-11-12 reorganized subsheets
    [RemBreak.kicad_sch, break_control.kicad_sch, control_unit.kicad_sch, power_control.kicad_sch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]
2024-11-12 project update - started drawing the first revision of the board
    [RemBreak.kicad_sch, break_control.kicad_sch, power_manager.kicad_sch, power_switch.kicad_sch]
2024-11-12 updated pcb - disabled header connector 3d models
    [USBcharger.kicad_pcb]
2024-11-12 updated usbcharger step - no header connectors
    [USBcharger.step]
2024-11-14 schematics drawing in progress
    [RemBreak.kicad_sch, break_control.kicad_sch, power_manager.kicad_sch, power_switch.kicad_sch]
2024-11-14 changes in power line sharing in progress
    [RemBreak.kicad_sch, break_control.kicad_sch, power_manager.kicad_sch, power_switch.kicad_sch]
2024-11-15 schematics development in progress
    [RemBreak.kicad_sch, break_control.kicad_sch, power_switch.kicad_sch]
2024-11-15 added step files to fill missing components on the pcb
    [LTC2943IDD#TRPBF.stp, S3B-XH-SM4-TB.step, SIS415DNT-T1-GE3.stp, TSM-106-01-L-DH-TR.stp]
2024-11-15 updated pcb and schematics - still in progress
    [RemBreak.kicad_pcb, RemBreak.kicad_sch, break_control.kicad_sch, power_manager.kicad_sch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]
2024-11-16 rf controller added crystal 3d model
    [RFController.kicad_pcb, RFController.kicad_sch]
2024-11-16 changed size of the board and development of schematic
    [RemBreak.kicad_pcb, RemBreak.kicad_sch, break_control.kicad_sch, power_switch.kicad_sch]
2024-11-16 added new step files required for full assembly
    [ECS-160-20-3X-TR.step, RFController.step]
2024-11-16 added RGB LED connection - missing connections in schematics
    [RemBreak.kicad_pcb, RemBreak.kicad_sch, power_manager.kicad_sch, power_switch.kicad_sch]
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2024-11-27 finished schematics routing and erc passed
    [RemBreak.kicad_pcb, RemBreak.kicad_sch, break_control.kicad_sch, power_manager.kicad_sch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]
2024-11-27 fixed errors in schematics
    [RemBreak.kicad_pcb, power_manager.kicad_sch]
2024-12-01 regenerated anotations and used battery connector with grounding
    [RemBreak.kicad_sch, break_control.kicad_sch, power_manager.kicad_sch, power_switch.kicad_sch]
2024-12-01 created 3mm band around the pcb and components grouped to be easily placed in the final layout
    [RemBreak.kicad_pcb]
2024-12-03 started routing of the pcb
    [RemBreak.kicad_pcb]
2024-12-05 routing in progress added new subsheet to easily swap signals at the control connector
    [RemBreak.kicad_pcb, RemBreak.kicad_sch, control_connector.kicad_sch, power_manager.kicad_sch]
2024-12-05 routing in progress
    [RemBreak.kicad_pcb, control_connector.kicad_sch]
2024-12-06 first version of routing finished
    [RemBreak.kicad_pcb, RemBreak.kicad_sch, break_control.kicad_sch, control_connector.kicad_sch]
2024-12-08 changed board settings and replaced r and c footprints with the ones for handsoldering
    [RemBreak.kicad_pcb, RemBreak.kicad_sch, break_control.kicad_sch, power_manager.kicad_sch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]
2024-12-09 partially reorganized components and routing
    [RemBreak.kicad_pcb, RemBreak.kicad_sch, control_connector.kicad_sch]
2024-12-10 components placed and tracks routed - missing gnd connections and have to refactor the resistors under MCU
    [RemBreak.kicad_pcb, break_control.kicad_sch, control_connector.kicad_sch]
2024-12-10 adjusting layout
    [RemBreak.kicad_pcb, break_control.kicad_sch]
2024-12-11 middle part rerouted to fix the gnd connection
    [RemBreak.kicad_pcb, RemBreak.kicad_sch, break_control.kicad_sch]
2024-12-12 finished routing - drc did not pass
    [RemBreak.kicad_pcb, RemBreak.kicad_sch, break_control.kicad_sch]
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2024-12-12 updated chinese modules footprints
    [RemBreak.kicad_pcb]
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2024-12-12 updated usb charger footprint
    [RemBreak.kicad_pcb]
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2024-12-12 updated footprints in the main pcb layout
    [RemBreak.kicad_pcb]
2024-12-14 changed minimum width for gnd poured copper
    [RemBreak.kicad_pcb]
2024-12-14 added pin description silkscreen labels
    [RemBreak.kicad_pcb]
2024-12-15 Note fonts changed to bold and added titles of the sheets included rev number
    [RemBreak.kicad_sch, break_control.kicad_sch, control_connector.kicad_sch, power_manager.kicad_sch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]
2024-12-23 rerouting in newer version of kicad
    [RemBreak.kicad_pcb]
2024-12-23 DRC passed, ignored certain packages which have small pitches
    [RemBreak.kicad_pcb]
2024-12-23 first version and added jumper to connect buzz internally not just through handlebars
    [RemBreak.kicad_pcb, RemBreak.kicad_sch, break_control.kicad_sch, control_connector.kicad_sch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]
2024-12-27 settings to generate gerber files
    [RemBreak.kicad_pcb]
2024-12-29 breakout boards to mill the pcbs for better pcb testing
    [breakoutpcbs.kicad_pcb, breakoutpcbs.kicad_sch, power_manager_bb.kicad_sch, power_switch_bb.kicad_sch]
2024-12-29 created grbjob files for breakoutpcbs and rembreak
    [RemBreak-job.gbrjob, RemBreak.kicad_pcb, breakoutpcbs-job.gbrjob]
2025-01-02 created two other modules to test the switching between charging and runnig mode
    [breakoutpcbs.kicad_pcb, breakoutpcbs.kicad_sch, power_switch_bbA.kicad_sch, power_switch_bbB.kicad_sch]
2025-01-02 this sheet has been split
    [power_switch_bb.kicad_sch]
2025-01-02 created three modules easy to solder and test the system functionality
    [breakoutpcbs-Edge_Cuts.gbr, breakoutpcbs-F_Cu.gbr, breakoutpcbs-job.gbrjob]
2025-01-06 updated schematics - added an extra ideal diode
    [RemBreak.kicad_sch, break_control.kicad_sch, control_connector.kicad_sch, power_manager.kicad_sch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]
2025-01-12 refactoring of the current boards and two added to test the whole circuit
    [battery_charger.kicad_sch, break_control.kicad_sch, breakoutpcbs.kicad_pcb, breakoutpcbs.kicad_sch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]
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2025-01-13 fixed wrong pinout on rf module and updated footprints
    [battery_charger.kicad_sch, break_control.kicad_sch, breakoutpcbs.kicad_pcb]
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2025-01-22 updated kicad version and updated todo list with different found issues
    [battery_charger.kicad_sch, break_control.kicad_sch, breakoutpcbs.kicad_sch, power_manager_bb.kicad_sch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]
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2025-02-21 added few components to fix indicator LED undefined cathode voltage and added vbus divider to match MCU voltage level
    [RemBrake.kicad_pcb, RemBrake.kicad_sch, brake_control.kicad_sch, control_connector.kicad_sch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]
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2025-03-12 fixed bugs with LED reverse current leakage and beeper deterministic startup delay
    [RemBrake.kicad_sch, brake_control.kicad_sch, control_connector.kicad_sch, power_manager.kicad_sch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]
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2025-03-15 replaced optocoupler with transistor and loaded components in the pcb sheet
    [RemBrake.kicad_pcb, RemBrake.kicad_sch, brake_control.kicad_sch, control_connector.kicad_sch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]
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2025-04-06 fixed issue with the buzzer sound when charging is finished
    [brake_control.kicad_sch, control_connector.kicad_sch, power_switch.kicad_sch]
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

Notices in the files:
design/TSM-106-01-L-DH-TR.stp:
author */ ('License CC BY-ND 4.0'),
